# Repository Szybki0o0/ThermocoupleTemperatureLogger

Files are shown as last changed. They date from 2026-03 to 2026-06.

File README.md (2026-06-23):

# Thermocouple Temperature Logger

Projekt sprzętowo-programowy precyzyjnego wielokanałowego rejestratora temperatury. Urządzenie służy do odczytu, wyświetlania oraz logowania danych pomiarowych z maksymalnie 8 termopar.

## 📌 Opis Projektu

Głównym zadaniem układu jest akwizycja danych z czujników temperatury za pomocą dedykowanego układu **LTC2983**, a następnie ich przetwarzanie na mikrokontrolerze **STM32H5**. System oferuje możliwość lokalnego zapisu pomiarów na kartę pamięci lub przesyłania ich do komputera PC za pośrednictwem sieci Ethernet w popularnym standardzie automatyki pomiarowej (SCPI / VISA).

Projekt jest obecnie w fazie rozwoju i obejmuje zarówno projekt elektroniki (PCB), jak i oprogramowania układowego (Firmware).

## ✨ Główne funkcjonalności

* **Precyzyjny pomiar:** Odczyt temperatur z 8 niezależnych termopar przy użyciu specjalizowanego układu LTC2983.
* **Logowanie danych:** Zapis historii pomiarów bezpośrednio na kartę pamięci MicroSD.
* **Komunikacja z PC:** Zdalny odczyt i sterowanie przez interfejs Ethernet z wykorzystaniem protokołu **VISA / SCPI**.
* **Podgląd na żywo:** Wyświetlanie aktualnych temperatur oraz stanu urządzenia na monochromatycznym ekranie LCD/OLED.
* **Interfejs użytkownika (HMI):** Wygodne sterowanie za pomocą enkodera obrotowego oraz dedykowanych przycisków umieszczonych pod wyświetlaczem.

## 🛠️ Architektura Sprzętowa (Hardware)

* **Mikrokontroler:** Rodzina STM32H563ZI (ARM Cortex-M33)
* **Układ pomiarowy:** Analog Devices LTC2983 (Multi-Sensor High Accuracy Digital Temperature Measurement System)
* **Wyświetlacz:** Monochromatyczny LCD / OLED
* **Interfejsy:** 
    * Gniazdo Ethernet (RJ45)
    * Slot na kartę pamięci uSD
    * Konfigurowalny panel przedni do podłączenia czujników temperatory
* **Sterowanie lokalne:** Enkoder obrotowy z przyciskiem + przyciski funkcyjne pod ekranem.
* **Zasilanie:** Zasilacz 230VAC → 5VDC-12VDC w postaci gotowego modułu na PCB lub wykorzystanie zasilania przez gniazdo DC.

## 💻 Oprogramowanie (Software)

* **System operacyjny (RTOS):** Eclipse ThreadX
* **Stos sieciowy:** Obsługa Ethernet do komunikacji z systemami nadrzędnymi.
* **Protokół komunikacyjny:** SCPI (Standard Commands for Programmable Instruments).
* **System plików:** Obsługa FAT/exFAT dla karty SD.

## 🚀 Status projektu

Hardware:
- [x] Konfiguracją peryferiów dla STM32H5
- [X] Schemat
- [X] projekt PCB
- [X] Montaż PCB
- [~] Uruchomienie PCB

Software:
- [X] Integracja systemu operacyjnego ThreadX
- [ ] Napisanie sterownika do obsługi LTC2983
- [X] Implementacją parsera komend SCPI
- [ ] Opracowaniem UI

## ➗ Podział prac
- Mateusz Gąsiorowski: 
  - Konfiguracja Peryferiów STM32
  - Schemat
  - Projekt PCB
  - Montaż i uruchomienie
 
- Jakub Konior:
  - Konfiguracja Peryferiów STM32
  - Schemat
  - Oprogramowanie

---
*Autorzy: Mateusz Gąsiorowski && Jakub Konior*

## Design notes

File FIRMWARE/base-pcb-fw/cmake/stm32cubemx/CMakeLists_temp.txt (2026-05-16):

cmake_minimum_required(VERSION 3.22)# Enable CMake support for ASM and C languagesenable_language(C CXX ASM)# STM32CubeMX generated symbols (macros)set(MX_Defines_Syms 	NX_INCLUDE_USER_DEFINE_FILE 	TX_INCLUDE_USER_DEFINE_FILE 	TX_SINGLE_MODE_NON_SECURE=1 	USE_HAL_DRIVER 	STM32H563xx    $<$<CONFIG:Debug>:DEBUG>)# STM32CubeMX generated include pathsset(MX_Include_Dirs    ${CMAKE_CURRENT_SOURCE_DIR}/../../Core/Inc    ${CMAKE_CURRENT_SOURCE_DIR}/../../NetXDuo/App    ${CMAKE_CURRENT_SOURCE_DIR}/../../NetXDuo/Target    ${CMAKE_CURRENT_SOURCE_DIR}/../../AZURE_RTOS/App    ${CMAKE_CURRENT_SOURCE_DIR}/../../Drivers/STM32H5xx_HAL_Driver/Inc    ${CMAKE_CURRENT_SOURCE_DIR}/../../Drivers/STM32H5xx_HAL_Driver/Inc/Legacy    ${CMAKE_CURRENT_SOURCE_DIR}/../../Drivers/BSP/Components/lan8742    ${CMAKE_CURRENT_SOURCE_DIR}/../../Middlewares/ST/netxduo/common/drivers/ethernet    ${CMAKE_CURRENT_SOURCE_DIR}/../../Middlewares/ST/threadx/common/inc    ${CMAKE_CURRENT_SOURCE_DIR}/../../Drivers/CMSIS/Device/ST/STM32H5xx/Include    ${CMAKE_CURRENT_SOURCE_DIR}/../../Middlewares/ST/netxduo/common/inc    ${CMAKE_CURRENT_SOURCE_DIR}/../../Middlewares/ST/netxduo/ports/cortex_m33/gnu/inc    ${CMAKE_CURRENT_SOURCE_DIR}/../../Middlewares/ST/threadx/ports/cortex_m33/gnu/inc    ${CMAKE_CURRENT_SOURCE_DIR}/../../Drivers/CMSIS/Include)# STM32CubeMX generated application sourcesset(MX_Application_Src    ${CMAKE_CURRENT_SOURCE_DIR}/../../NetXDuo/App/app_netxduo.c    ${CMAKE_CURRENT_SOURCE_DIR}/../../AZURE_RTOS/App/app_azure_rtos.c    ${CMAKE_CURRENT_SOURCE_DIR}/../../Core/Src/tx_initialize_low_level.S    ${CMAKE_CURRENT_SOURCE_DIR}/../../Core/Src/main.cpp    ${CMAKE_CURRENT_SOURCE_DIR}/../../Core/Src/gpio.c    ${CMAKE_CURRENT_SOURCE_DIR}/../../Core/Src/eth.c    ${CMAKE_CURRENT_SOURCE_DIR}/../../Core/Src/gpdma.c    ${CMAKE_CURRENT_SOURCE_DIR}/../../Core/Src/i2c.c    ${CMAKE_CURRENT_SOURCE_DIR}/../../Core/Src/sdmmc.c    ${CMAKE_CURRENT_SOURCE_DIR}/../../Core/Src/spi.c    ${CMAKE_CURRENT_SOURCE_DIR}/../../Core/Src/app_threadx.c    ${CMAKE_CURRENT_SOURCE_DIR}/../../Core/Src/tim.c    ${CMAKE_CURRENT_SOURCE_DIR}/../../Core/Src/stm32h5xx_it.c    ${CMAKE_CURRENT_SOURCE_DIR}/../../Core/Src/stm32h5xx_hal_msp.c    ${CMAKE_CURRENT_SOURCE_DIR}/../../Core/Src/sysmem.c    ${CMAKE_CURRENT_SOURCE_DIR}/../../Core/Src/syscalls.c    ${CMAKE_CURRENT_SOURCE_DIR}/../../startup_stm32h563xx.s)# STM32 HAL/LL Driversset(STM32_Drivers_Src    ${CMAKE_CURRENT_SOURCE_DIR}/../../Core/Src/system_stm32h5xx.c    ${CMAKE_CURRENT_SOURCE_DIR}/../../Drivers/STM32H5xx_HAL_Driver/Src/stm32h5xx_hal_cortex.c    ${CMAKE_CURRENT_SOURCE_DIR}/../../Drivers/STM32H5xx_HAL_Driver/Src/stm32h5xx_hal_rcc.c    ${CMAKE_CURRENT_SOURCE_DIR}/../../Drivers/STM32H5xx_HAL_Driver/Src/stm32h5xx_hal_rcc_ex.c    ${CMAKE_CURRENT_SOURCE_DIR}/../../Drivers/STM32H5xx_HAL_Driver/Src/stm32h5xx_hal_flash.c    ${CMAKE_CURRENT_SOURCE_DIR}/../../Drivers/STM32H5xx_HAL_Driver/Src/stm32h5xx_hal_flash_ex.c    ${CMAKE_CURRENT_SOURCE_DIR}/../../Drivers/STM32H5xx_HAL_Driver/Src/stm32h5xx_hal_gpio.c    ${CMAKE_CURRENT_SOURCE_DIR}/../../Drivers/STM32H5xx_HAL_Driver/Src/stm32h5xx_hal_dma.c    ${CMAKE_CURRENT_SOURCE_DIR}/../../Drivers/STM32H5xx_HAL_Driver/Src/stm32h5xx_hal_dma_ex.c    ${CMAKE_CURRENT_SOURCE_DIR}/../../Drivers/STM32H5xx_HAL_Driver/Src/stm32h5xx_hal_pwr.c    ${CMAKE_CURRENT_SOURCE_DIR}/../../Drivers/STM32H5xx_HAL_Driver/Src/stm32h5xx_hal_pwr_ex.c    ${CMAKE_CURRENT_SOURCE_DIR}/../../Drivers/STM32H5xx_HAL_Driver/Src/stm32h5xx_hal.c    ${CMAKE_CURRENT_SOURCE_DIR}/../../Drivers/STM32H5xx_HAL_Driver/Src/stm32h5xx_hal_exti.c    ${CMAKE_CURRENT_SOURCE_DIR}/../../Drivers/STM32H5xx_HAL_Driver/Src/stm32h5xx_hal_eth.c    ${CMAKE_CURRENT_SOURCE_DIR}/../../Drivers/STM32H5xx_HAL_Driver/Src/stm32h5xx_hal_eth_ex.c    ${CMAKE_CURRENT_SOURCE_DIR}/../../Drivers/STM32H5xx_HAL_Driver/Src/stm32h5xx_hal_i2c.c    ${CMAKE_CURRENT_SOURCE_DIR}/../../Drivers/STM32H5xx_HAL_Driver/Src/stm32h5xx_hal_i2c_ex.c    ${CMAKE_CURRENT_SOURCE_DIR}/../../Drivers/STM32H5xx_HAL_Driver/Src/stm32h5xx_ll_sdmmc.c    ${CMAKE_CURRENT_SOURCE_DIR}/../../Drivers/STM32H5xx_HAL_Driver/Src/stm32h5xx_ll_dlyb.c    ${CMAKE_CURRENT_SOURCE_DIR}/../../Drivers/STM32H5xx_HAL_Driver/Src/stm32h5xx_hal_sd.c    ${CMAKE_CURRENT_SOURCE_DIR}/../../Drivers/STM32H5xx_HAL_Driver/Src/stm32h5xx_hal_sd_ex.c    ${CMAKE_CURRENT_SOURCE_DIR}/../../Drivers/STM32H5xx_HAL_Driver/Src/stm32h5xx_hal_mmc.c    ${CMAKE_CURRENT_SOURCE_DIR}/../../Drivers/STM32H5xx_HAL_Driver/Src/stm32h5xx_hal_mmc_ex.c    ${CMAKE_CURRENT_SOURCE_DIR}/../../Drivers/STM32H5xx_HAL_Driver/Src/stm32h5xx_hal_sdio.c    ${CMAKE_CURRENT_SOURCE_DIR}/../../Drivers/STM32H5xx_HAL_Driver/Src/stm32h5xx_hal_spi.c    ${CMAKE_CURRENT_SOURCE_DIR}/../../Drivers/STM32H5xx_HAL_Driver/Src/stm32h5xx_hal_spi_ex.c    ${CMAKE_CURRENT_SOURCE_DIR}/../../Drivers/STM32H5xx_HAL_Driver/Src/stm32h5xx_hal_tim.c    ${CMAKE_CURRENT_SOURCE_DIR}/../../Drivers/STM32H5xx_HAL_Driver/Src/stm32h5xx_hal_tim_ex.c    ${CMAKE_CURRENT_SOURCE_DIR}/../../Drivers/BSP/Components/lan8742/lan8742.c)# Drivers Midllewaresset(ThreadX_Src    ${CMAKE_CURRENT_SOURCE_DIR}/../../Middlewares/ST/threadx/ports/cortex_m33/gnu/src/tx_thread_context_restore.S    ${CMAKE_CURRENT_SOURCE_DIR}/../../Middlewares/ST/threadx/ports/cortex_m33/gnu/src/tx_thread_context_save.S    ${CMAKE_CURRENT_SOURCE_DIR}/../../Middlewares/ST/threadx/ports/cortex_m33/gnu/src/tx_thread_interrupt_control.S    ${CMAKE_CURRENT_SOURCE_DIR}/../../Middlewares/ST/threadx/ports/cortex_m33/gnu/src/tx_thread_interrupt_disable.S    ${CMAKE_CURRENT_SOURCE_DIR}/../../Middlewares/ST/threadx/ports/cortex_m33/gnu/src/tx_thread_interrupt_restore.S    ${CMAKE_CURRENT_SOURCE_DIR}/../../Middlewares/ST/threadx/ports/cortex_m33/gnu/src/tx_thread_schedule.S    ${CMAKE_CURRENT_SOURCE_DIR}/../../Middlewares/ST/threadx/ports/cortex_m33/gnu/src/tx_thread_stack_build.S    ${CMAKE_CURRENT_SOURCE_DIR}/../../Middlewares/ST/threadx/ports/cortex_m33/gnu/src/tx_thread_system_return.S    ${CMAKE_CURRENT_SOURCE_DIR}/../../Middlewares/ST/threadx/ports/cortex_m33/gnu/src/tx_timer_interrupt.S    ${CMAKE_CURRENT_SOURCE_DIR}/../../Middlewares/ST/threadx/common/src/tx_initialize_high_level.c    ${CMAKE_CURRENT_SOURCE_DIR}/../../Middlewares/ST/threadx/common/src/tx_initialize_kernel_enter.c    ${CMAKE_CURRENT_SOURCE_DIR}/../../Middlewares/ST/threadx/common/src/tx_initialize_kernel_setup.c    ${CMAKE_CURRENT_SOURCE_DIR}/../../Middlewares/ST/threadx/common/src/tx_thread_stack_error_handler.c    ${CMAKE_CURRENT_SOURCE_DIR}/../../Middlewares/ST/threadx/common/src/tx_thread_stack_error_notify.c    ${CMAKE_CURRENT_SOURCE_DIR}/../../Middlewares/ST/threadx/common/src/tx_thread_system_resume.c    ${CMAKE_CURRENT_SOURCE_DIR}/../../Middlewares/ST/threadx/common/src/tx_block_allocate.c    ${CMAKE_CURRENT_SOURCE_DIR}/../../Middlewares/ST/threadx/common/src/tx_block_pool_cleanup.c    ${CMAKE_CURRENT_SOURCE_DIR}/../../Middlewares/ST/threadx/common/src/tx_block_pool_create.c    ${CMAKE_CURRENT_SOURCE_DIR}/../../Middlewares/ST/threadx/common/src/tx_block_pool_delete.c    ${CMAKE_CURRENT_SOURCE_DIR}/../../Middlewares/ST/threadx/common/src/tx_block_pool_info_get.c    ${CMAKE_CURRENT_SOURCE_DIR}/../../Middlewares/ST/threadx/common/src/tx_block_pool_initialize.c    ${CMAKE_CURRENT_SOURCE_DIR}/../../Middlewares/ST/threadx/common/src/tx_block_pool_prioritize.c    ${CMAKE_CURRENT_SOURCE_DIR}/../../Middlewares/ST/threadx/common/src/tx_block_release.c    ${CMAKE_CURRENT_SOURCE_DIR}/../../Middlewares/ST/threadx/common/src/tx_byte_allocate.c    ${CMAKE_CURRENT_SOURCE_DIR}/../../Middlewares/ST/threadx/common/src/tx_byte_pool_cleanup.c    ${CMAKE_CURRENT_SOURCE_DIR}/../../Middlewares/ST/threadx/common/src/tx_byte_pool_create.c    ${CMAKE_CURRENT_SOURCE_DIR}/../../Middlewares/ST/threadx/common/src/tx_byte_pool_delete.c    ${CMAKE_CURRENT_SOURCE_DIR}/../../Middlewares/ST/threadx/common/src/tx_byte_pool_info_get.c    ${CMAKE_CURRENT_SOURCE_DIR}/../../Middlewares/ST/threadx/common/src/tx_byte_pool_initialize.c    ${CMAKE_CURRENT_SOURCE_DIR}/../../Middlewares/ST/threadx/common/src/tx_byte_pool_prioritize.c    ${CMAKE_CURRENT_SOURCE_DIR}/../../Middlewares/ST/threadx/common/src/tx_byte_pool_search.c    ${CMAKE_CURRENT_SOURCE_DIR}/../../Middlewares/ST/threadx/common/src/tx_byte_release.c    ${CMAKE_CURRENT_SOURCE_DIR}/../../Middlewares/ST/threadx/common/src/tx_event_flags_cleanup.c    ${CMAKE_CURRENT_SOURCE_DIR}/../../Middlewares/ST/threadx/common/src/tx_event_flags_create.c    ${CMAKE_CURRENT_SOURCE_DIR}/../../Middlewares/ST/threadx/common/src/tx_event_flags_delete.c    ${CMAKE_CURRENT_SOURCE_DIR}/../../Middlewares/ST/threadx/common/src/tx_event_flags_get.c    ${CMAKE_CURRENT_SOURCE_DIR}/../../Middlewares/ST/threadx/common/src/tx_event_flags_info_get.c    ${CMAKE_CURRENT_SOURCE_DIR}/../../Middlewares/ST/threadx/common/src/tx_event_flags_initialize.c    ${CMAKE_CURRENT_SOURCE_DIR}/../../Middlewares/ST/threadx/common/src/tx_event_flags_set.c    ${CMAKE_CURRENT_SOURCE_DIR}/../../Middlewares/ST/threadx/common/src/tx_event_flags_set_notify.c    ${CMAKE_CURRENT_SOURCE_DIR}/../../Middlewares/ST/threadx/common/src/tx_mutex_cleanup.c    ${CMAKE_CURRENT_SOURCE_DIR}/../../Middlewares/ST/threadx/common/src/tx_mutex_create.c    ${CMAKE_CURRENT_SOURCE_DIR}/../../Middlewares/ST/threadx/common/src/tx_mutex_delete.c    ${CMAKE_CURRENT_SOURCE_DIR}/../../Middlewares/ST/threadx/common/src/tx_mutex_get.c    ${CMAKE_CURRENT_SOURCE_DIR}/../../Middlewares/ST/threadx/common/src/tx_mutex_info_get.c    ${CMAKE_CURRENT_SOURCE_DIR}/../../Middlewares/ST/threadx/common/src/tx_mutex_initialize.c    ${CMAKE_CURRENT_SOURCE_DIR}/../../Middlewares/ST/threadx/common/src/tx_mutex_prioritize.c    ${CMAKE_CURRENT_SOURCE_DIR}/../../Middlewares/ST/threadx/common/src/tx_mutex_priority_change.c    ${CMAKE_CURRENT_SOURCE_DIR}/../../Middlewares/ST/threadx/common/src/tx_mutex_put.c    ${CMAKE_CURRENT_SOURCE_DIR}/../../Middlewares/ST/threadx/common/src/tx_queue_cleanup.c    ${CMAKE_CURRENT_SOURCE_DIR}/../../Middlewares/ST/threadx/common/src/tx_queue_create.c    ${CMAKE_CURRENT_SOURCE_DIR}/../../Middlewares/ST/threadx/common/src/tx_queue_delete.c    ${CMAKE_CURRENT_SOURCE_DIR}/../../Middlewares/ST/threadx/common/src/tx_queue_flush.c    ${CMAKE_CURRENT_SOURCE_DIR}/../../Middlewares/ST/threadx/common/src/tx_queue_front_send.c    ${CMAKE_CURRENT_SOURCE_DIR}/../../Middlewares/ST/threadx/common/src/tx_queue_info_get.c    ${CMAKE_CURRENT_SOURCE_DIR}/../../Middlewares/ST/threadx/common/src/tx_queue_initialize.c    ${CMAKE_CURRENT_SOURCE_DIR}/../../Middlewares/ST/threadx/common/src/tx_queue_prioritize.c    ${CMAKE_CURRENT_SOURCE_DIR}/../../Middlewares/ST/threadx/common/src/tx_queue_receive.c    ${CMAKE_CURRENT_SOURCE_DIR}/../../Middlewares/ST/threadx/common/src/tx_queue_send.c    ${CMAKE_CURRENT_SOURCE_DIR}/../../Middlewares/ST/threadx/common/src/tx_queue_send_notify.c    ${CMAKE_CURRENT_SOURCE_DIR}/../../Middlewares/ST/threadx/common/src/tx_semaphore_ceiling_put.c    ${CMAKE_CURRENT_SOURCE_DIR}/../../Middlewares/ST/threadx/common/src/tx_semaphore_cleanup.c    ${CMAKE_CURRENT_SOURCE_DIR}/../../Middlewares/ST/threadx/common/src/tx_semaphore_create.c    ${CMAKE_CURRENT_SOURCE_DIR}/../../Middlewares/ST/threadx/common/src/tx_semaphore_delete.c    ${CMAKE_CURRENT_SOURCE_DIR}/../../Middlewares/ST/threadx/common/src/tx_semaphore_get.c    ${CMAKE_CURRENT_SOURCE_DIR}/../../Middlewares/ST/threadx/common/src/tx_semaphore_info_get.c    ${CMAKE_CURRENT_SOURCE_DIR}/../../Middlewares/ST/threadx/common/src/tx_semaphore_initialize.c    ${CMAKE_CURRENT_SOURCE_DIR}/../../Middlewares/ST/threadx/common/src/tx_semaphore_prioritize.c    ${CMAKE_CURRENT_SOURCE_DIR}/../../Middlewares/ST/threadx/common/src/tx_semaphore_put.c    ${CMAKE_CURRENT_SOURCE_DIR}/../../Middlewares/ST/threadx/common/src/tx_semaphore_put_notify.c    ${CMAKE_CURRENT_SOURCE_DIR}/../../Middlewares/ST/threadx/common/src/tx_thread_create.c    ${CMAKE_CURRENT_SOURCE_DIR}/../../Middlewares/ST/threadx/common/src/tx_thread_delete.c    ${CMAKE_CURRENT_SOURCE_DIR}/../../Middlewares/ST/threadx/common/src/tx_thread_entry_exit_notify.c    ${CMAKE_CURRENT_SOURCE_DIR}/../../Middlewares/ST/threadx/common/src/tx_thread_identify.c    ${CMAKE_CURRENT_SOURCE_DIR}/../../Middlewares/ST/threadx/common/src/tx_thread_info_get.c    ${CMAKE_CURRENT_SOURCE_DIR}/../../Middlewares/ST/threadx/common/src/tx_thread_initialize.c    ${CMAKE_CURRENT_SOURCE_DIR}/../../Middlewares/ST/threadx/common/src/tx_thread_preemption_change.c    ${CMAKE_CURRENT_SOURCE_DIR}/../../Middlewares/ST/threadx/common/src/tx_thread_priority_change.c    ${CMAKE_CURRENT_SOURCE_DIR}/../../Middlewares/ST/threadx/common/src/tx_thread_relinquish.c    ${CMAKE_CURRENT_SOURCE_DIR}/../../Middlewares/ST/threadx/common/src/tx_thread_reset.c    ${CMAKE_CURRENT_SOURCE_DIR}/../../Middlewares/ST/threadx/common/src/tx_thread_resume.c    ${CMAKE_CURRENT_SOURCE_DIR}/../../Middlewares/ST/threadx/common/src/tx_thread_shell_entry.c    ${CMAKE_CURRENT_SOURCE_DIR}/../../Middlewares/ST/threadx/common/src/tx_thread_sleep.c    ${CMAKE_CURRENT_SOURCE_DIR}/../../Middlewares/ST/threadx/common/src/tx_thread_stack_analyze.c    ${CMAKE_CURRENT_SOURCE_DIR}/../../Middlewares/ST/threadx/common/src/tx_thread_suspend.c    ${CMAKE_CURRENT_SOURCE_DIR}/../../Middlewares/ST/threadx/common/src/tx_thread_system_preempt_check.c    ${CMAKE_CURRENT_SOURCE_DIR}/../../Middlewares/ST/threadx/common/src/tx_thread_system_suspend.c    ${CMAKE_CURRENT_SOURCE_DIR}/../../Middlewares/ST/threadx/common/src/tx_thread_terminate.c    ${CMAKE_CURRENT_SOURCE_DIR}/../../Middlewares/ST/threadx/common/src/tx_thread_time_slice.c    ${CMAKE_CURRENT_SOURCE_DIR}/../../Middlewares/ST/threadx/common/src/tx_thread_time_slice_change.c    ${CMAKE_CURRENT_SOURCE_DIR}/../../Middlewares/ST/threadx/common/src/tx_thread_timeout.c    ${CMAKE_CURRENT_SOURCE_DIR}/../../Middlewares/ST/threadx/common/src/tx_thread_wait_abort.c    ${CMAKE_CURRENT_SOURCE_DIR}/../../Middlewares/ST/threadx/common/src/tx_time_get.c    ${CMAKE_CURRENT_SOURCE_DIR}/../../Middlewares/ST/threadx/common/src/tx_time_set.c    ${CMAKE_CURRENT_SOURCE_DIR}/../../Middlewares/ST/threadx/common/src/txe_block_allocate.c    ${CMAKE_CURRENT_SOURCE_DIR}/../../Middlewares/ST/threadx/common/src/txe_block_pool_create.c    ${CMAKE_CURRENT_SOURCE_DIR}/../../Middlewares/ST/threadx/common/src/txe_block_pool_delete.c    ${CMAKE_CURRENT_SOURCE_DIR}/../../Middlewares/ST/threadx/common/src/txe_block_pool_info_get.c    ${CMAKE_CURRENT_SOURCE_DIR}/../../Middlewares/ST/threadx/common/src/txe_block_pool_prioritize.c    ${CMAKE_CURRENT_SOURCE_DIR}/../../Middlewares/ST/threadx/common/src/txe_block_release.c    ${CMAKE_CURRENT_SOURCE_DIR}/../../Middlewares/ST/threadx/common/src/txe_byte_allocate.c    ${CMAKE_CURRENT_SOURCE_DIR}/../../Middlewares/ST/threadx/common/src/txe_byte_pool_create.c    ${CMAKE_CURRENT_SOURCE_DIR}/../../Middlewares/ST/threadx/common/src/txe_byte_pool_delete.c    ${CMAKE_CURRENT_SOURCE_DIR}/../../Middlewares/ST/threadx/common/src/txe_byte_pool_info_get.c    ${CMAKE_CURRENT_SOURCE_DIR}/../../Middlewares/ST/threadx/common/src/txe_byte_pool_prioritize.c    ${CMAKE_CURRENT_SOURCE_DIR}/../../Middlewares/ST/threadx/common/src/txe_byte_release.c    ${CMAKE_CURRENT_SOURCE_DIR}/../../Middlewares/ST/threadx/common/src/txe_event_flags_create.c    ${CMAKE_CURRENT_SOURCE_DIR}/../../Middlewares/ST/threadx/common/src/txe_event_flags_delete.c    ${CMAKE_CURRENT_SOURCE_DIR}/../../Middlewares/ST/threadx/common/src/txe_event_flags_get.c    ${CMAKE_CURRENT_SOURCE_DIR}/../../Middlewares/ST/threadx/common/src/txe_event_flags_info_get.c    ${CMAKE_CURRENT_SOURCE_DIR}/../../Middlewares/ST/threadx/common/src/txe_event_flags_set.c    ${CMAKE_CURRENT_SOURCE_DIR}/../../Middlewares/ST/threadx/common/src/txe_event_flags_set_notify.c    ${CMAKE_CURRENT_SOURCE_DIR}/../../Middlewares/ST/threadx/common/src/txe_mutex_create.c    ${CMAKE_CURRENT_SOURCE_DIR}/../../Middlewares/ST/threadx/common/src/txe_mutex_delete.c    ${CMAKE_CURRENT_SOURCE_DIR}/../../Middlewares/ST/threadx/common/src/txe_mutex_get.c    ${CMAKE_CURRENT_SOURCE_DIR}/../../Middlewares/ST/threadx/common/src/txe_mutex_info_get.c    ${CMAKE_CURRENT_SOURCE_DIR}/../../Middlewares/ST/threadx/common/src/txe_mutex_prioritize.c    ${CMAKE_CURRENT_SOURCE_DIR}/../../Middlewares/ST/threadx/common/src/txe_mutex_put.c    ${CMAKE_CURRENT_SOURCE_DIR}/../../Middlewares/ST/threadx/common/src/txe_queue_create.c    ${CMAKE_CURRENT_SOURCE_DIR}/../../Middlewares/ST/threadx/common/src/txe_queue_delete.c    ${CMAKE_CURRENT_SOURCE_DIR}/../../Middlewares/ST/threadx/common/src/txe_queue_flush.c    ${CMAKE_CURRENT_SOURCE_DIR}/../../Middlewares/ST/threadx/common/src/txe_queue_front_send.c    ${CMAKE_CURRENT_SOURCE_DIR}/../../Middlewares/ST/threadx/common/src/txe_queue_info_get.c    ${CMAKE_CURRENT_SOURCE_DIR}/../../Middlewares/ST/threadx/common/src/txe_queue_prioritize.c    ${CMAKE_CURRENT_SOURCE_DIR}/../../Middlewares/ST/threadx/common/src/txe_queue_receive.c    ${CMAKE_CURRENT_SOURCE_DIR}/../../Middlewares/ST/threadx/common/src/txe_queue_send.c    ${CMAKE_CURRENT_SOURCE_DIR}/../../Middlewares/ST/threadx/common/src/txe_queue_send_notify.c    ${CMAKE_CURRENT_SOURCE_DIR}/../../Middlewares/ST/threadx/common/src/txe_semaphore_ceiling_put.c    ${CMAKE_CURRENT_SOURCE_DIR}/../../Middlewares/ST/threadx/common/src/txe_semaphore_create.c    ${CMAKE_CURRENT_SOURCE_DIR}/../../Middlewares/ST/threadx/common/src/txe_semaphore_delete.c    ${CMAKE_CURRENT_SOURCE_DIR}/../../Middlewares/ST/threadx/common/src/txe_semaphore_get.c    ${CMAKE_CURRENT_SOURCE_DIR}/../../Middlewares/ST/threadx/common/src/txe_semaphore_info_get.c    ${CMAKE_CURRENT_SOURCE_DIR}/../../Middlewares/ST/threadx/common/src/txe_semaphore_prioritize.c    ${CMAKE_CURRENT_SOURCE_DIR}/../../Middlewares/ST/threadx/common/src/txe_semaphore_put.c    ${CMAKE_CURRENT_SOURCE_DIR}/../../Middlewares/ST/threadx/common/src/txe_semaphore_put_notify.c    ${CMAKE_CURRENT_SOURCE_DIR}/../../Middlewares/ST/threadx/common/src/txe_thread_create.c    ${CMAKE_CURRENT_SOURCE_DIR}/../../Middlewares/ST/threadx/common/src/txe_thread_delete.c    ${CMAKE_CURRENT_SOURCE_DIR}/../../Middlewares/ST/threadx/common/src/txe_thread_entry_exit_notify.c    ${CMAKE_CURRENT_SOURCE_DIR}/../../Middlewares/ST/threadx/common/src/txe_thread_info_get.c    ${CMAKE_CURRENT_SOURCE_DIR}/../../Middlewares/ST/threadx/common/src/txe_thread_preemption_change.c    ${CMAKE_CURRENT_SOURCE_DIR}/../../Middlewares/ST/threadx/common/src/txe_thread_priority_change.c    ${CMAKE_CURRENT_SOURCE_DIR}/../../Middlewares/ST/threadx/common/src/txe_thread_relinquish.c    ${CMAKE_CURRENT_SOURCE_DIR}/../../Middlewares/ST/threadx/common/src/txe_thread_reset.c    ${CMAKE_CURRENT_SOURCE_DIR}/../../Middlewares/ST/threadx/common/src/txe_thread_resume.c    ${CMAKE_CURRENT_SOURCE_DIR}/../../Middlewares/ST/threadx/common/src/txe_thread_suspend.c    ${CMAKE_CURRENT_SOURCE_DIR}/../../Middlewares/ST/threadx/common/src/txe_thread_terminate.c    ${CMAKE_CURRENT_SOURCE_DIR}/../../Middlewares/ST/threadx/common/src/txe_thread_time_slice_change.c    ${CMAKE_CURRENT_SOURCE_DIR}/../../Middlewares/ST/threadx/common/src/txe_thread_wait_abort.c    ${CMAKE_CURRENT_SOURCE_DIR}/../../Middlewares/ST/threadx/common/src/tx_timer_activate.c    ${CMAKE_CURRENT_SOURCE_DIR}/../../Middlewares/ST/threadx/common/src/tx_timer_change.c    ${CMAKE_CURRENT_SOURCE_DIR}/../../Middlewares/ST/threadx/common/src/tx_timer_create.c    ${CMAKE_CURRENT_SOURCE_DIR}/../../Middlewares/ST/threadx/common/src/tx_timer_deactivate.c    ${CMAKE_CURRENT_SOURCE_DIR}/../../Middlewares/ST/threadx/common/src/tx_timer_delete.c    ${CMAKE_CURRENT_SOURCE_DIR}/../../Middlewares/ST/threadx/common/src/tx_timer_expiration_process.c    ${CMAKE_CURRENT_SOURCE_DIR}/../../Middlewares/ST/threadx/common/src/tx_timer_info_get.c    ${CMAKE_CURRENT_SOURCE_DIR}/../../Middlewares/ST/threadx/common/src/tx_timer_initialize.c    ${CMAKE_CURRENT_SOURCE_DIR}/../../Middlewares/ST/threadx/common/src/tx_timer_system_activate.c    ${CMAKE_CURRENT_SOURCE_DIR}/../../Middlewares/ST/threadx/common/src/tx_timer_system_deactivate.c    ${CMAKE_CURRENT_SOURCE_DIR}/../../Middlewares/ST/threadx/common/src/tx_timer_thread_entry.c    ${CMAKE_CURRENT_SOURCE_DIR}/../../Middlewares/ST/threadx/common/src/txe_timer_activate.c    ${CMAKE_CURRENT_SOURCE_DIR}/../../Middlewares/ST/threadx/common/src/txe_timer_change.c    ${CMAKE_CURRENT_SOURCE_DIR}/../../Middlewares/ST/threadx/common/src/txe_timer_create.c    ${CMAKE_CURRENT_SOURCE_DIR}/../../Middlewares/ST/threadx/common/src/txe_timer_deactivate.c    ${CMAKE_CURRENT_SOURCE_DIR}/../../Middlewares/ST/threadx/common/src/txe_timer_delete.c    ${CMAKE_CURRENT_SOURCE_DIR}/../../Middlewares/ST/threadx/common/src/txe_timer_info_get.c)set(NetXDuo_Src    ${CMAKE_CURRENT_SOURCE_DIR}/../../Middlewares/ST/netxduo/common/drivers/ethernet/nx_stm32_eth_driver.c    ${CMAKE_CURRENT_SOURCE_DIR}/../../Middlewares/ST/netxduo/common/src/nx_arp_announce_send.c    ${CMAKE_CURRENT_SOURCE_DIR}/../../Middlewares/ST/netxduo/common/src/nx_arp_dynamic_entries_invalidate.c    ${CMAKE_CURRENT_SOURCE_DIR}/../../Middlewares/ST/netxduo/common/src/nx_arp_dynamic_entry_delete.c    ${CMAKE_CURRENT_SOURCE_DIR}/../../Middlewares/ST/netxduo/common/src/nx_arp_dynamic_entry_set.c    ${CMAKE_CURRENT_SOURCE_DIR}/../../Middlewares/ST/netxduo/common/src/nx_arp_enable.c    ${CMAKE_CURRENT_SOURCE_DIR}/../../Middlewares/ST/netxduo/common/src/nx_arp_entry_allocate.c    ${CMAKE_CURRENT_SOURCE_DIR}/../../Middlewares/ST/netxduo/common/src/nx_arp_entry_delete.c    ${CMAKE_CURRENT_SOURCE_DIR}/../../Middlewares/ST/netxduo/common/src/nx_arp_gratuitous_send.c    ${CMAKE_CURRENT_SOURCE_DIR}/../../Middlewares/ST/netxduo/common/src/nx_arp_hardware_address_find.c    ${CMAKE_CURRENT_SOURCE_DIR}/../../Middlewares/ST/netxduo/common/src/nx_arp_info_get.c    ${CMAKE_CURRENT_SOURCE_DIR}/../../Middlewares/ST/netxduo/common/src/nx_arp_initialize.c    ${CMAKE_CURRENT_SOURCE_DIR}/../../Middlewares/ST/netxduo/common/src/nx_arp_interface_entries_delete.c    ${CMAKE_CURRENT_SOURCE_DIR}/../../Middlewares/ST/netxduo/common/src/nx_arp_ip_address_find.c    ${CMAKE_CURRENT_SOURCE_DIR}/../../Middlewares/ST/netxduo/common/src/nx_arp_packet_deferred_receive.c    ${CMAKE_CURRENT_SOURCE_DIR}/../../Middlewares/ST/netxduo/common/src/nx_arp_packet_receive.c    ${CMAKE_CURRENT_SOURCE_DIR}/../../Middlewares/ST/netxduo/common/src/nx_arp_packet_send.c    ${CMAKE_CURRENT_SOURCE_DIR}/../../Middlewares/ST/netxduo/common/src/nx_arp_periodic_update.c    ${CMAKE_CURRENT_SOURCE_DIR}/../../Middlewares/ST/netxduo/common/src/nx_arp_probe_send.c    ${CMAKE_CURRENT_SOURCE_DIR}/../../Middlewares/ST/netxduo/common/src/nx_arp_queue_process.c    ${CMAKE_CURRENT_SOURCE_DIR}/../../Middlewares/ST/netxduo/common/src/nx_arp_queue_send.c    ${CMAKE_CURRENT_SOURCE_DIR}/../../Middlewares/ST/netxduo/common/src/nx_arp_static_entries_delete.c    ${CMAKE_CURRENT_SOURCE_DIR}/../../Middlewares/ST/netxduo/common/src/nx_arp_static_entry_create.c    ${CMAKE_CURRENT_SOURCE_DIR}/../../Middlewares/ST/netxduo/common/src/nx_arp_static_entry_delete.c    ${CMAKE_CURRENT_SOURCE_DIR}/../../Middlewares/ST/netxduo/common/src/nx_arp_static_entry_delete_internal.c    ${CMAKE_CURRENT_SOURCE_DIR}/../../Middlewares/ST/netxduo/common/src/nx_icmp_cleanup.c    ${CMAKE_CURRENT_SOURCE_DIR}/../../Middlewares/ST/netxduo/common/src/nx_icmp_enable.c    ${CMAKE_CURRENT_SOURCE_DIR}/../../Middlewares/ST/netxduo/common/src/nx_icmp_info_get.c    ${CMAKE_CURRENT_SOURCE_DIR}/../../Middlewares/ST/netxduo/common/src/nx_icmp_interface_ping.c    ${CMAKE_CURRENT_SOURCE_DIR}/../../Middlewares/ST/netxduo/common/src/nx_icmp_interface_ping6.c    ${CMAKE_CURRENT_SOURCE_DIR}/../../Middlewares/ST/netxduo/common/src/nx_icmp_packet_process.c    ${CMAKE_CURRENT_SOURCE_DIR}/../../Middlewares/ST/netxduo/common/src/nx_icmp_packet_receive.c    ${CMAKE_CURRENT_SOURCE_DIR}/../../Middlewares/ST/netxduo/common/src/nx_icmp_ping.c    ${CMAKE_CURRENT_SOURCE_DIR}/../../Middlewares/ST/netxduo/common/src/nx_icmp_queue_process.c    ${CMAKE_CURRENT_SOURCE_DIR}/../../Middlewares/ST/netxduo/common/src/nx_icmpv4_packet_process.c    ${CMAKE_CURRENT_SOURCE_DIR}/../../Middlewares/ST/netxduo/common/src/nx_icmpv4_process_echo_reply.c    ${CMAKE_CURRENT_SOURCE_DIR}/../../Middlewares/ST/netxduo/common/src/nx_icmpv4_process_echo_request.c    ${CMAKE_CURRENT_SOURCE_DIR}/../../Middlewares/ST/netxduo/common/src/nx_icmpv4_send_error_message.c    ${CMAKE_CURRENT_SOURCE_DIR}/../../Middlewares/ST/netxduo/common/src/nx_igmp_enable.c    ${CMAKE_CURRENT_SOURCE_DIR}/../../Middlewares/ST/netxduo/common/src/nx_igmp_info_get.c    ${CMAKE_CURRENT_SOURCE_DIR}/../../Middlewares/ST/netxduo/common/src/nx_igmp_interface_report_send.c    ${CMAKE_CURRENT_SOURCE_DIR}/../../Middlewares/ST/netxduo/common/src/nx_igmp_loopback_disable.c    ${CMAKE_CURRENT_SOURCE_DIR}/../../Middlewares/ST/netxduo/common/src/nx_igmp_loopback_enable.c    ${CMAKE_CURRENT_SOURCE_DIR}/../../Middlewares/ST/netxduo/common/src/nx_igmp_multicast_check.c    ${CMAKE_CURRENT_SOURCE_DIR}/../../Middlewares/ST/netxduo/common/src/nx_igmp_multicast_interface_join.c    ${CMAKE_CURRENT_SOURCE_DIR}/../../Middlewares/ST/netxduo/common/src/nx_igmp_multicast_interface_join_internal.c    ${CMAKE_CURRENT_SOURCE_DIR}/../../Middlewares/ST/netxduo/common/src/nx_igmp_multicast_interface_leave.c    ${CMAKE_CURRENT_SOURCE_DIR}/../../Middlewares/ST/netxduo/common/src/nx_igmp_multicast_interface_leave_internal.c    ${CMAKE_CURRENT_SOURCE_DIR}/../../Middlewares/ST/netxduo/common/src/nx_igmp_multicast_join.c    ${CMAKE_CURRENT_SOURCE_DIR}/../../Middlewares/ST/netxduo/common/src/nx_igmp_multicast_leave.c    ${CMAKE_CURRENT_SOURCE_DIR}/../../Middlewares/ST/netxduo/common/src/nx_igmp_packet_process.c    ${CMAKE_CURRENT_SOURCE_DIR}/../../Middlewares/ST/netxduo/common/src/nx_igmp_packet_receive.c    ${CMAKE_CURRENT_SOURCE_DIR}/../../Middlewares/ST/netxduo/common/src/nx_igmp_periodic_processing.c    ${CMAKE_CURRENT_SOURCE_DIR}/../../Middlewares/ST/netxduo/common/src/nx_igmp_queue_process.c    ${CMAKE_CURRENT_SOURCE_DIR}/../../Middlewares/ST/netxduo/common/src/nx_invalidate_destination_entry.c    ${CMAKE_CURRENT_SOURCE_DIR}/../../Middlewares/ST/netxduo/common/src/nx_ip_address_change_notify.c    ${CMAKE_CURRENT_SOURCE_DIR}/../../Middlewares/ST/netxduo/common/src/nx_ip_address_get.c    ${CMAKE_CURRENT_SOURCE_DIR}/../../Middlewares/ST/netxduo/common/src/nx_ip_address_set.c    ${CMAKE_CURRENT_SOURCE_DIR}/../../Middlewares/ST/netxduo/common/src/nx_ip_auxiliary_packet_pool_set.c    ${CMAKE_CURRENT_SOURCE_DIR}/../../Middlewares/ST/netxduo/common/src/nx_ip_checksum_compute.c    ${CMAKE_CURRENT_SOURCE_DIR}/../../Middlewares/ST/netxduo/common/src/nx_ip_create.c    ${CMAKE_CURRENT_SOURCE_DIR}/../../Middlewares/ST/netxduo/common/src/nx_ip_deferred_link_status_process.c    ${CMAKE_CURRENT_SOURCE_DIR}/../../Middlewares/ST/netxduo/common/src/nx_ip_delete.c    ${CMAKE_CURRENT_SOURCE_DIR}/../../Middlewares/ST/netxduo/common/src/nx_ip_delete_queue_clear.c    ${CMAKE_CURRENT_SOURCE_DIR}/../../Middlewares/ST/netxduo/common/src/nx_ip_dispatch_process.c    ${CMAKE_CURRENT_SOURCE_DIR}/../../Middlewares/ST/netxduo/common/src/nx_ip_driver_deferred_enable.c    ${CMAKE_CURRENT_SOURCE_DIR}/../../Middlewares/ST/netxduo/common/src/nx_ip_driver_deferred_processing.c    ${CMAKE_CURRENT_SOURCE_DIR}/../../Middlewares/ST/netxduo/common/src/nx_ip_driver_deferred_receive.c    ${CMAKE_CURRENT_SOURCE_DIR}/../../Middlewares/ST/netxduo/common/src/nx_ip_driver_direct_command.c    ${CMAKE_CURRENT_SOURCE_DIR}/../../Middlewares/ST/netxduo/common/src/nx_ip_driver_interface_direct_command.c    ${CMAKE_CURRENT_SOURCE_DIR}/../../Middlewares/ST/netxduo/common/src/nx_ip_driver_link_status_event.c    ${CMAKE_CURRENT_SOURCE_DIR}/../../Middlewares/ST/netxduo/common/src/nx_ip_driver_packet_send.c    ${CMAKE_CURRENT_SOURCE_DIR}/../../Middlewares/ST/netxduo/common/src/nx_ip_fast_periodic_timer_entry.c    ${CMAKE_CURRENT_SOURCE_DIR}/../../Middlewares/ST/netxduo/common/src/nx_ip_forward_packet_process.c    ${CMAKE_CURRENT_SOURCE_DIR}/../../Middlewares/ST/netxduo/common/src/nx_ip_forwarding_disable.c    ${CMAKE_CURRENT_SOURCE_DIR}/../../Middlewares/ST/netxduo/common/src/nx_ip_forwarding_enable.c    ${CMAKE_CURRENT_SOURCE_DIR}/../../Middlewares/ST/netxduo/common/src/nx_ip_fragment_assembly.c    ${CMAKE_CURRENT_SOURCE_DIR}/../../Middlewares/ST/netxduo/common/src/nx_ip_fragment_disable.c    ${CMAKE_CURRENT_SOURCE_DIR}/../../Middlewares/ST/netxduo/common/src/nx_ip_fragment_enable.c    ${CMAKE_CURRENT_SOURCE_DIR}/../../Middlewares/ST/netxduo/common/src/nx_ip_fragment_forward_packet.c    ${CMAKE_CURRENT_SOURCE_DIR}/../../Middlewares/ST/netxduo/common/src/nx_ip_fragment_packet.c    ${CMAKE_CURRENT_SOURCE_DIR}/../../Middlewares/ST/netxduo/common/src/nx_ip_fragment_timeout_check.c    ${CMAKE_CURRENT_SOURCE_DIR}/../../Middlewares/ST/netxduo/common/src/nx_ip_gateway_address_clear.c    ${CMAKE_CURRENT_SOURCE_DIR}/../../Middlewares/ST/netxduo/common/src/nx_ip_gateway_address_get.c    ${CMAKE_CURRENT_SOURCE_DIR}/../../Middlewares/ST/netxduo/common/src/nx_ip_gateway_address_set.c    ${CMAKE_CURRENT_SOURCE_DIR}/../../Middlewares/ST/netxduo/common/src/nx_ip_header_add.c    ${CMAKE_CURRENT_SOURCE_DIR}/../../Middlewares/ST/netxduo/common/src/nx_ip_info_get.c    ${CMAKE_CURRENT_SOURCE_DIR}/../../Middlewares/ST/netxduo/common/src/nx_ip_initialize.c    ${CMAKE_CURRENT_SOURCE_DIR}/../../Middlewares/ST/netxduo/common/src/nx_ip_interface_address_get.c    ${CMAKE_CURRENT_SOURCE_DIR}/../../Middlewares/ST/netxduo/common/src/nx_ip_interface_address_mapping_configure.c    ${CMAKE_CURRENT_SOURCE_DIR}/../../Middlewares/ST/netxduo/common/src/nx_ip_interface_address_set.c    ${CMAKE_CURRENT_SOURCE_DIR}/../../Middlewares/ST/netxduo/common/src/nx_ip_interface_attach.c    ${CMAKE_CURRENT_SOURCE_DIR}/../../Middlewares/ST/netxduo/common/src/nx_ip_interface_capability_get.c    ${CMAKE_CURRENT_SOURCE_DIR}/../../Middlewares/ST/netxduo/common/src/nx_ip_interface_capability_set.c    ${CMAKE_CURRENT_SOURCE_DIR}/../../Middlewares/ST/netxduo/common/src/nx_ip_interface_detach.c    ${CMAKE_CURRENT_SOURCE_DIR}/../../Middlewares/ST/netxduo/common/src/nx_ip_interface_info_get.c    ${CMAKE_CURRENT_SOURCE_DIR}/../../Middlewares/ST/netxduo/common/src/nx_ip_interface_mtu_set.c    ${CMAKE_CURRENT_SOURCE_DIR}/../../Middlewares/ST/netxduo/common/src/nx_ip_interface_physical_address_get.c    ${CMAKE_CURRENT_SOURCE_DIR}/../../Middlewares/ST/netxduo/common/src/nx_ip_interface_physical_address_set.c    ${CMAKE_CURRENT_SOURCE_DIR}/../../Middlewares/ST/netxduo/common/src/nx_ip_interface_status_check.c    ${CMAKE_CURRENT_SOURCE_DIR}/../../Middlewares/ST/netxduo/common/src/nx_ip_link_status_change_notify_set.c    ${CMAKE_CURRENT_SOURCE_DIR}/../../Middlewares/ST/netxduo/common/src/nx_ip_max_payload_size_find.c    ${CMAKE_CURRENT_SOURCE_DIR}/../../Middlewares/ST/netxduo/common/src/nx_ip_packet_checksum_compute.c    ${CMAKE_CURRENT_SOURCE_DIR}/../../Middlewares/ST/netxduo/common/src/nx_ip_packet_deferred_receive.c    ${CMAKE_CURRENT_SOURCE_DIR}/../../Middlewares/ST/netxduo/common/src/nx_ip_packet_receive.c    ${CMAKE_CURRENT_SOURCE_DIR}/../../Middlewares/ST/netxduo/common/src/nx_ip_packet_send.c    ${CMAKE_CURRENT_SOURCE_DIR}/../../Middlewares/ST/netxduo/common/src/nx_ip_periodic_timer_entry.c    ${CMAKE_CURRENT_SOURCE_DIR}/../../Middlewares/ST/netxduo/common/src/nx_ip_raw_packet_cleanup.c    ${CMAKE_CURRENT_SOURCE_DIR}/../../Middlewares/ST/netxduo/common/src/nx_ip_raw_packet_disable.c    ${CMAKE_CURRENT_SOURCE_DIR}/../../Middlewares/ST/netxduo/common/src/nx_ip_raw_packet_enable.c    ${CMAKE_CURRENT_SOURCE_DIR}/../../Middlewares/ST/netxduo/common/src/nx_ip_raw_packet_filter_set.c    ${CMAKE_CURRENT_SOURCE_DIR}/../../Middlewares/ST/netxduo/common/src/nx_ip_raw_packet_processing.c    ${CMAKE_CURRENT_SOURCE_DIR}/../../Middlewares/ST/netxduo/common/src/nx_ip_raw_packet_receive.c    ${CMAKE_CURRENT_SOURCE_DIR}/../../Middlewares/ST/netxduo/common/src/nx_ip_raw_packet_send.c    ${CMAKE_CURRENT_SOURCE_DIR}/../../Middlewares/ST/netxduo/common/src/nx_ip_raw_packet_source_send.c    ${CMAKE_CURRENT_SOURCE_DIR}/../../Middlewares/ST/netxduo/common/src/nx_ip_raw_receive_queue_max_set.c    ${CMAKE_CURRENT_SOURCE_DIR}/../../Middlewares/ST/netxduo/common/src/nx_ip_route_find.c    ${CMAKE_CURRENT_SOURCE_DIR}/../../Middlewares/ST/netxduo/common/src/nx_ip_static_route_add.c    ${CMAKE_CURRENT_SOURCE_DIR}/../../Middlewares/ST/netxduo/common/src/nx_ip_static_route_delete.c    ${CMAKE_CURRENT_SOURCE_DIR}/../../Middlewares/ST/netxduo/common/src/nx_ip_status_check.c    ${CMAKE_CURRENT_SOURCE_DIR}/../../Middlewares/ST/netxduo/common/src/nx_ip_thread_entry.c    ${CMAKE_CURRENT_SOURCE_DIR}/../../Middlewares/ST/netxduo/common/src/nx_ipv4_multicast_interface_join.c    ${CMAKE_CURRENT_SOURCE_DIR}/../../Middlewares/ST/netxduo/common/src/nx_ipv4_multicast_interface_leave.c    ${CMAKE_CURRENT_SOURCE_DIR}/../../Middlewares/ST/netxduo/common/src/nx_ipv4_option_process.c    ${CMAKE_CURRENT_SOURCE_DIR}/../../Middlewares/ST/netxduo/common/src/nx_ipv4_packet_receive.c    ${CMAKE_CURRENT_SOURCE_DIR}/../../Middlewares/ST/netxduo/common/src/nx_md5.c    ${CMAKE_CURRENT_SOURCE_DIR}/../../Middlewares/ST/netxduo/common/src/nx_packet_allocate.c    ${CMAKE_CURRENT_SOURCE_DIR}/../../Middlewares/ST/netxduo/common/src/nx_packet_copy.c    ${CMAKE_CURRENT_SOURCE_DIR}/../../Middlewares/ST/netxduo/common/src/nx_packet_data_adjust.c    ${CMAKE_CURRENT_SOURCE_DIR}/../../Middlewares/ST/netxduo/common/src/nx_packet_data_append.c    ${CMAKE_CURRENT_SOURCE_DIR}/../../Middlewares/ST/netxduo/common/src/nx_packet_data_extract_offset.c    ${CMAKE_CURRENT_SOURCE_DIR}/../../Middlewares/ST/netxduo/common/src/nx_packet_data_retrieve.c    ${CMAKE_CURRENT_SOURCE_DIR}/../../Middlewares/ST/netxduo/common/src/nx_packet_debug_info_get.c    ${CMAKE_CURRENT_SOURCE_DIR}/../../Middlewares/ST/netxduo/common/src/nx_packet_length_get.c    ${CMAKE_CURRENT_SOURCE_DIR}/../../Middlewares/ST/netxduo/common/src/nx_packet_pool_cleanup.c    ${CMAKE_CURRENT_SOURCE_DIR}/../../Middlewares/ST/netxduo/common/src/nx_packet_pool_create.c    ${CMAKE_CURRENT_SOURCE_DIR}/../../Middlewares/ST/netxduo/common/src/nx_packet_pool_delete.c    ${CMAKE_CURRENT_SOURCE_DIR}/../../Middlewares/ST/netxduo/common/src/nx_packet_pool_info_get.c    ${CMAKE_CURRENT_SOURCE_DIR}/../../Middlewares/ST/netxduo/common/src/nx_packet_pool_initialize.c    ${CMAKE_CURRENT_SOURCE_DIR}/../../Middlewares/ST/netxduo/common/src/nx_packet_pool_low_watermark_set.c    ${CMAKE_CURRENT_SOURCE_DIR}/../../Middlewares/ST/netxduo/common/src/nx_packet_release.c    ${CMAKE_CURRENT_SOURCE_DIR}/../../Middlewares/ST/netxduo/common/src/nx_packet_transmit_release.c    ${CMAKE_CURRENT_SOURCE_DIR}/../../Middlewares/ST/netxduo/common/src/nx_rarp_disable.c    ${CMAKE_CURRENT_SOURCE_DIR}/../../Middlewares/ST/netxduo/common/src/nx_rarp_enable.c    ${CMAKE_CURRENT_SOURCE_DIR}/../../Middlewares/ST/netxduo/common/src/nx_rarp_info_get.c    ${CMAKE_CURRENT_SOURCE_DIR}/../../Middlewares/ST/netxduo/common/src/nx_rarp_packet_deferred_receive.c    ${CMAKE_CURRENT_SOURCE_DIR}/../../Middlewares/ST/netxduo/common/src/nx_rarp_packet_receive.c    ${CMAKE_CURRENT_SOURCE_DIR}/../../Middlewares/ST/netxduo/common/src/nx_rarp_packet_send.c    ${CMAKE_CURRENT_SOURCE_DIR}/../../Middlewares/ST/netxduo/common/src/nx_rarp_periodic_update.c    ${CMAKE_CURRENT_SOURCE_DIR}/../../Middlewares/ST/netxduo/common/src/nx_rarp_queue_process.c    ${CMAKE_CURRENT_SOURCE_DIR}/../../Middlewares/ST/netxduo/common/src/nx_system_initialize.c    ${CMAKE_CURRENT_SOURCE_DIR}/../../Middlewares/ST/netxduo/common/src/nx_tcp_cleanup_deferred.c    ${CMAKE_CURRENT_SOURCE_DIR}/../../Middlewares/ST/netxduo/common/src/nx_tcp_client_bind_cleanup.c    ${CMAKE_CURRENT_SOURCE_DIR}/../../Middlewares/ST/netxduo/common/src/nx_tcp_client_socket_bind.c    ${CMAKE_CURRENT_SOURCE_DIR}/../../Middlewares/ST/netxduo/common/src/nx_tcp_client_socket_connect.c    ${CMAKE_CURRENT_SOURCE_DIR}/../../Middlewares/ST/netxduo/common/src/nx_tcp_client_socket_port_get.c    ${CMAKE_CURRENT_SOURCE_DIR}/../../Middlewares/ST/netxduo/common/src/nx_tcp_client_socket_unbind.c    ${CMAKE_CURRENT_SOURCE_DIR}/../../Middlewares/ST/netxduo/common/src/nx_tcp_connect_cleanup.c    ${CMAKE_CURRENT_SOURCE_DIR}/../../Middlewares/ST/netxduo/common/src/nx_tcp_deferred_cleanup_check.c    ${CMAKE_CURRENT_SOURCE_DIR}/../../Middlewares/ST/netxduo/common/src/nx_tcp_disconnect_cleanup.c    ${CMAKE_CURRENT_SOURCE_DIR}/../../Middlewares/ST/netxduo/common/src/nx_tcp_enable.c    ${CMAKE_CURRENT_SOURCE_DIR}/../../Middlewares/ST/netxduo/common/src/nx_tcp_fast_periodic_processing.c    ${CMAKE_CURRENT_SOURCE_DIR}/../../Middlewares/ST/netxduo/common/src/nx_tcp_free_port_find.c    ${CMAKE_CURRENT_SOURCE_DIR}/../../Middlewares/ST/netxduo/common/src/nx_tcp_info_get.c    ${CMAKE_CURRENT_SOURCE_DIR}/../../Middlewares/ST/netxduo/common/src/nx_tcp_initialize.c    ${CMAKE_CURRENT_SOURCE_DIR}/../../Middlewares/ST/netxduo/common/src/nx_tcp_mss_option_get.c    ${CMAKE_CURRENT_SOURCE_DIR}/../../Middlewares/ST/netxduo/common/src/nx_tcp_no_connection_reset.c    ${CMAKE_CURRENT_SOURCE_DIR}/../../Middlewares/ST/netxduo/common/src/nx_tcp_packet_process.c    ${CMAKE_CURRENT_SOURCE_DIR}/../../Middlewares/ST/netxduo/common/src/nx_tcp_packet_receive.c    ${CMAKE_CURRENT_SOURCE_DIR}/../../Middlewares/ST/netxduo/common/src/nx_tcp_packet_send_ack.c    ${CMAKE_CURRENT_SOURCE_DIR}/../../Middlewares/ST/netxduo/common/src/nx_tcp_packet_send_control.c    ${CMAKE_CURRENT_SOURCE_DIR}/../../Middlewares/ST/netxduo/common/src/nx_tcp_packet_send_fin.c    ${CMAKE_CURRENT_SOURCE_DIR}/../../Middlewares/ST/netxduo/common/src/nx_tcp_packet_send_probe.c    ${CMAKE_CURRENT_SOURCE_DIR}/../../Middlewares/ST/netxduo/common/src/nx_tcp_packet_send_rst.c    ${CMAKE_CURRENT_SOURCE_DIR}/../../Middlewares/ST/netxduo/common/src/nx_tcp_packet_send_syn.c    ${CMAKE_CURRENT_SOURCE_DIR}/../../Middlewares/ST/netxduo/common/src/nx_tcp_periodic_processing.c    ${CMAKE_CURRENT_SOURCE_DIR}/../../Middlewares/ST/netxduo/common/src/nx_tcp_queue_process.c    ${CMAKE_CURRENT_SOURCE_DIR}/../../Middlewares/ST/netxduo/common/src/nx_tcp_receive_cleanup.c    ${CMAKE_CURRENT_SOURCE_DIR}/../../Middlewares/ST/netxduo/common/src/nx_tcp_server_socket_accept.c    ${CMAKE_CURRENT_SOURCE_DIR}/../../Middlewares/ST/netxduo/common/src/nx_tcp_server_socket_listen.c    ${CMAKE_CURRENT_SOURCE_DIR}/../../Middlewares/ST/netxduo/common/src/nx_tcp_server_socket_relisten.c    ${CMAKE_CURRENT_SOURCE_DIR}/../../Middlewares/ST/netxduo/common/src/nx_tcp_server_socket_unaccept.c    ${CMAKE_CURRENT_SOURCE_DIR}/../../Middlewares/ST/netxduo/common/src/nx_tcp_server_socket_unlisten.c    ${CMAKE_CURRENT_SOURCE_DIR}/../../Middlewares/ST/netxduo/common/src/nx_tcp_socket_block_cleanup.c    ${CMAKE_CURRENT_SOURCE_DIR}/../../Middlewares/ST/netxduo/common/src/nx_tcp_socket_bytes_available.c    ${CMAKE_CURRENT_SOURCE_DIR}/../../Middlewares/ST/netxduo/common/src/nx_tcp_socket_connection_reset.c    ${CMAKE_CURRENT_SOURCE_DIR}/../../Middlewares/ST/netxduo/common/src/nx_tcp_socket_create.c    ${CMAKE_CURRENT_SOURCE_DIR}/../../Middlewares/ST/netxduo/common/src/nx_tcp_socket_delete.c    ${CMAKE_CURRENT_SOURCE_DIR}/../../Middlewares/ST/netxduo/common/src/nx_tcp_socket_disconnect.c    ${CMAKE_CURRENT_SOURCE_DIR}/../../Middlewares/ST/netxduo/common/src/nx_tcp_socket_disconnect_complete_notify.c    ${CMAKE_CURRENT_SOURCE_DIR}/../../Middlewares/ST/netxduo/common/src/nx_tcp_socket_establish_notify.c    ${CMAKE_CURRENT_SOURCE_DIR}/../../Middlewares/ST/netxduo/common/src/nx_tcp_socket_info_get.c    ${CMAKE_CURRENT_SOURCE_DIR}/../../Middlewares/ST/netxduo/common/src/nx_tcp_socket_mss_get.c    ${CMAKE_CURRENT_SOURCE_DIR}/../../Middlewares/ST/netxduo/common/src/nx_tcp_socket_mss_peer_get.c    ${CMAKE_CURRENT_SOURCE_DIR}/../../Middlewares/ST/netxduo/common/src/nx_tcp_socket_mss_set.c    ${CMAKE_CURRENT_SOURCE_DIR}/../../Middlewares/ST/netxduo/common/src/nx_tcp_socket_packet_process.c    ${CMAKE_CURRENT_SOURCE_DIR}/../../Middlewares/ST/netxduo/common/src/nx_tcp_socket_peer_info_get.c    ${CMAKE_CURRENT_SOURCE_DIR}/../../Middlewares/ST/netxduo/common/src/nx_tcp_socket_queue_depth_notify_set.c    ${CMAKE_CURRENT_SOURCE_DIR}/../../Middlewares/ST/netxduo/common/src/nx_tcp_socket_receive.c    ${CMAKE_CURRENT_SOURCE_DIR}/../../Middlewares/ST/netxduo/common/src/nx_tcp_socket_receive_notify.c    ${CMAKE_CURRENT_SOURCE_DIR}/../../Middlewares/ST/netxduo/common/src/nx_tcp_socket_receive_queue_flush.c    ${CMAKE_CURRENT_SOURCE_DIR}/../../Middlewares/ST/netxduo/common/src/nx_tcp_socket_receive_queue_max_set.c    ${CMAKE_CURRENT_SOURCE_DIR}/../../Middlewares/ST/netxduo/common/src/nx_tcp_socket_retransmit.c    ${CMAKE_CURRENT_SOURCE_DIR}/../../Middlewares/ST/netxduo/common/src/nx_tcp_socket_send.c    ${CMAKE_CURRENT_SOURCE_DIR}/../../Middlewares/ST/netxduo/common/src/nx_tcp_socket_send_internal.c    ${CMAKE_CURRENT_SOURCE_DIR}/../../Middlewares/ST/netxduo/common/src/nx_tcp_socket_state_ack_check.c    ${CMAKE_CURRENT_SOURCE_DIR}/../../Middlewares/ST/netxduo/common/src/nx_tcp_socket_state_closing.c    ${CMAKE_CURRENT_SOURCE_DIR}/../../Middlewares/ST/netxduo/common/src/nx_tcp_socket_state_data_check.c    ${CMAKE_CURRENT_SOURCE_DIR}/../../Middlewares/ST/netxduo/common/src/nx_tcp_socket_state_established.c    ${CMAKE_CURRENT_SOURCE_DIR}/../../Middlewares/ST/netxduo/common/src/nx_tcp_socket_state_fin_wait1.c    ${CMAKE_CURRENT_SOURCE_DIR}/../../Middlewares/ST/netxduo/common/src/nx_tcp_socket_state_fin_wait2.c    ${CMAKE_CURRENT_SOURCE_DIR}/../../Middlewares/ST/netxduo/common/src/nx_tcp_socket_state_last_ack.c    ${CMAKE_CURRENT_SOURCE_DIR}/../../Middlewares/ST/netxduo/common/src/nx_tcp_socket_state_syn_received.c    ${CMAKE_CURRENT_SOURCE_DIR}/../../Middlewares/ST/netxduo/common/src/nx_tcp_socket_state_syn_sent.c    ${CMAKE_CURRENT_SOURCE_DIR}/../../Middlewares/ST/netxduo/common/src/nx_tcp_socket_state_transmit_check.c    ${CMAKE_CURRENT_SOURCE_DIR}/../../Middlewares/ST/netxduo/common/src/nx_tcp_socket_state_wait.c    ${CMAKE_CURRENT_SOURCE_DIR}/../../Middlewares/ST/netxduo/common/src/nx_tcp_socket_thread_resume.c    ${CMAKE_CURRENT_SOURCE_DIR}/../../Middlewares/ST/netxduo/common/src/nx_tcp_socket_thread_suspend.c    ${CMAKE_CURRENT_SOURCE_DIR}/../../Middlewares/ST/netxduo/common/src/nx_tcp_socket_timed_wait_callback.c    ${CMAKE_CURRENT_SOURCE_DIR}/../../Middlewares/ST/netxduo/common/src/nx_tcp_socket_transmit_configure.c    ${CMAKE_CURRENT_SOURCE_DIR}/../../Middlewares/ST/netxduo/common/src/nx_tcp_socket_transmit_queue_flush.c    ${CMAKE_CURRENT_SOURCE_DIR}/../../Middlewares/ST/netxduo/common/src/nx_tcp_socket_window_update_notify_set.c    ${CMAKE_CURRENT_SOURCE_DIR}/../../Middlewares/ST/netxduo/common/src/nx_tcp_transmit_cleanup.c    ${CMAKE_CURRENT_SOURCE_DIR}/../../Middlewares/ST/netxduo/common/src/nx_tcp_window_scaling_option_get.c    ${CMAKE_CURRENT_SOURCE_DIR}/../../Middlewares/ST/netxduo/common/src/nx_udp_bind_cleanup.c    ${CMAKE_CURRENT_SOURCE_DIR}/../../Middlewares/ST/netxduo/common/src/nx_udp_enable.c    ${CMAKE_CURRENT_SOURCE_DIR}/../../Middlewares/ST/netxduo/common/src/nx_udp_free_port_find.c    ${CMAKE_CURRENT_SOURCE_DIR}/../../Middlewares/ST/netxduo/common/src/nx_udp_info_get.c    ${CMAKE_CURRENT_SOURCE_DIR}/../../Middlewares/ST/netxduo/common/src/nx_udp_packet_info_extract.c    ${CMAKE_CURRENT_SOURCE_DIR}/../../Middlewares/ST/netxduo/common/src/nx_udp_packet_receive.c    ${CMAKE_CURRENT_SOURCE_DIR}/../../Middlewares/ST/netxduo/common/src/nx_udp_receive_cleanup.c    ${CMAKE_CURRENT_SOURCE_DIR}/../../Middlewares/ST/netxduo/common/src/nx_udp_socket_bind.c    ${CMAKE_CURRENT_SOURCE_DIR}/../../Middlewares/ST/netxduo/common/src/nx_udp_socket_bytes_available.c    ${CMAKE_CURRENT_SOURCE_DIR}/../../Middlewares/ST/netxduo/common/src/nx_udp_socket_checksum_disable.c    ${CMAKE_CURRENT_SOURCE_DIR}/../../Middlewares/ST/netxduo/common/src/nx_udp_socket_checksum_enable.c    ${CMAKE_CURRENT_SOURCE_DIR}/../../Middlewares/ST/netxduo/common/src/nx_udp_socket_create.c    ${CMAKE_CURRENT_SOURCE_DIR}/../../Middlewares/ST/netxduo/common/src/nx_udp_socket_delete.c    ${CMAKE_CURRENT_SOURCE_DIR}/../../Middlewares/ST/netxduo/common/src/nx_udp_socket_info_get.c    ${CMAKE_CURRENT_SOURCE_DIR}/../../Middlewares/ST/netxduo/common/src/nx_udp_socket_port_get.c    ${CMAKE_CURRENT_SOURCE_DIR}/../../Middlewares/ST/netxduo/common/src/nx_udp_socket_receive.c    ${CMAKE_CURRENT_SOURCE_DIR}/../../Middlewares/ST/netxduo/common/src/nx_udp_socket_receive_notify.c    ${CMAKE_CURRENT_SOURCE_DIR}/../../Middlewares/ST/netxduo/common/src/nx_udp_socket_send.c    ${CMAKE_CURRENT_SOURCE_DIR}/../../Middlewares/ST/netxduo/common/src/nx_udp_socket_source_send.c    ${CMAKE_CURRENT_SOURCE_DIR}/../../Middlewares/ST/netxduo/common/src/nx_udp_socket_unbind.c    ${CMAKE_CURRENT_SOURCE_DIR}/../../Middlewares/ST/netxduo/common/src/nx_udp_source_extract.c    ${CMAKE_CURRENT_SOURCE_DIR}/../../Middlewares/ST/netxduo/common/src/nx_utility.c    ${CMAKE_CURRENT_SOURCE_DIR}/../../Middlewares/ST/netxduo/common/src/nxd_icmp_enable.c    ${CMAKE_CURRENT_SOURCE_DIR}/../../Middlewares/ST/netxduo/common/src/nxd_icmp_ping.c    ${CMAKE_CURRENT_SOURCE_DIR}/../../Middlewares/ST/netxduo/common/src/nxd_icmp_source_ping.c    ${CMAKE_CURRENT_SOURCE_DIR}/../../Middlewares/ST/netxduo/common/src/nxd_ip_raw_packet_send.c    ${CMAKE_CURRENT_SOURCE_DIR}/../../Middlewares/ST/netxduo/common/src/nxd_ip_raw_packet_source_send.c    ${CMAKE_CURRENT_SOURCE_DIR}/../../Middlewares/ST/netxduo/common/src/nxd_tcp_client_socket_connect.c    ${CMAKE_CURRENT_SOURCE_DIR}/../../Middlewares/ST/netxduo/common/src/nxd_tcp_socket_peer_info_get.c    ${CMAKE_CURRENT_SOURCE_DIR}/../../Middlewares/ST/netxduo/common/src/nxd_udp_packet_info_extract.c    ${CMAKE_CURRENT_SOURCE_DIR}/../../Middlewares/ST/netxduo/common/src/nxd_udp_socket_send.c    ${CMAKE_CURRENT_SOURCE_DIR}/../../Middlewares/ST/netxduo/common/src/nxd_udp_socket_source_send.c    ${CMAKE_CURRENT_SOURCE_DIR}/../../Middlewares/ST/netxduo/common/src/nxd_udp_source_extract.c    ${CMAKE_CURRENT_SOURCE_DIR}/../../Middlewares/ST/netxduo/common/src/nxde_icmp_enable.c    ${CMAKE_CURRENT_SOURCE_DIR}/../../Middlewares/ST/netxduo/common/src/nxde_icmp_ping.c    ${CMAKE_CURRENT_SOURCE_DIR}/../../Middlewares/ST/netxduo/common/src/nxde_icmp_source_ping.c    ${CMAKE_CURRENT_SOURCE_DIR}/../../Middlewares/ST/netxduo/common/src/nxde_ip_raw_packet_send.c    ${CMAKE_CURRENT_SOURCE_DIR}/../../Middlewares/ST/netxduo/common/src/nxde_ip_raw_packet_source_send.c    ${CMAKE_CURRENT_SOURCE_DIR}/../../Middlewares/ST/netxduo/common/src/nxde_tcp_client_socket_connect.c    ${CMAKE_CURRENT_SOURCE_DIR}/../../Middlewares/ST/netxduo/common/src/nxde_tcp_socket_peer_info_get.c    ${CMAKE_CURRENT_SOURCE_DIR}/../../Middlewares/ST/netxduo/common/src/nxde_udp_packet_info_extract.c    ${CMAKE_CURRENT_SOURCE_DIR}/../../Middlewares/ST/netxduo/common/src/nxde_udp_socket_send.c    ${CMAKE_CURRENT_SOURCE_DIR}/../../Middlewares/ST/netxduo/common/src/nxde_udp_socket_source_send.c    ${CMAKE_CURRENT_SOURCE_DIR}/../../Middlewares/ST/netxduo/common/src/nxde_udp_source_extract.c    ${CMAKE_CURRENT_SOURCE_DIR}/../../Middlewares/ST/netxduo/common/src/nxe_arp_dynamic_entries_invalidate.c    ${CMAKE_CURRENT_SOURCE_DIR}/../../Middlewares/ST/netxduo/common/src/nxe_arp_dynamic_entry_set.c    ${CMAKE_CURRENT_SOURCE_DIR}/../../Middlewares/ST/netxduo/common/src/nxe_arp_enable.c    ${CMAKE_CURRENT_SOURCE_DIR}/../../Middlewares/ST/netxduo/common/src/nxe_arp_entry_delete.c    ${CMAKE_CURRENT_SOURCE_DIR}/../../Middlewares/ST/netxduo/common/src/nxe_arp_gratuitous_send.c    ${CMAKE_CURRENT_SOURCE_DIR}/../../Middlewares/ST/netxduo/common/src/nxe_arp_hardware_address_find.c    ${CMAKE_CURRENT_SOURCE_DIR}/../../Middlewares/ST/netxduo/common/src/nxe_arp_info_get.c    ${CMAKE_CURRENT_SOURCE_DIR}/../../Middlewares/ST/netxduo/common/src/nxe_arp_ip_address_find.c    ${CMAKE_CURRENT_SOURCE_DIR}/../../Middlewares/ST/netxduo/common/src/nxe_arp_static_entries_delete.c    ${CMAKE_CURRENT_SOURCE_DIR}/../../Middlewares/ST/netxduo/common/src/nxe_arp_static_entry_create.c    ${CMAKE_CURRENT_SOURCE_DIR}/../../Middlewares/ST/netxduo/common/src/nxe_arp_static_entry_delete.c    ${CMAKE_CURRENT_SOURCE_DIR}/../../Middlewares/ST/netxduo/common/src/nxe_icmp_enable.c    ${CMAKE_CURRENT_SOURCE_DIR}/../../Middlewares/ST/netxduo/common/src/nxe_icmp_info_get.c    ${CMAKE_CURRENT_SOURCE_DIR}/../../Middlewares/ST/netxduo/common/src/nxe_icmp_ping.c    ${CMAKE_CURRENT_SOURCE_DIR}/../../Middlewares/ST/netxduo/common/src/nxe_igmp_enable.c    ${CMAKE_CURRENT_SOURCE_DIR}/../../Middlewares/ST/netxduo/common/src/nxe_igmp_info_get.c    ${CMAKE_CURRENT_SOURCE_DIR}/../../Middlewares/ST/netxduo/common/src/nxe_igmp_loopback_disable.c    ${CMAKE_CURRENT_SOURCE_DIR}/../../Middlewares/ST/netxduo/common/src/nxe_igmp_loopback_enable.c    ${CMAKE_CURRENT_SOURCE_DIR}/../../Middlewares/ST/netxduo/common/src/nxe_igmp_multicast_interface_join.c    ${CMAKE_CURRENT_SOURCE_DIR}/../../Middlewares/ST/netxduo/common/src/nxe_igmp_multicast_interface_leave.c    ${CMAKE_CURRENT_SOURCE_DIR}/../../Middlewares/ST/netxduo/common/src/nxe_igmp_multicast_join.c    ${CMAKE_CURRENT_SOURCE_DIR}/../../Middlewares/ST/netxduo/common/src/nxe_igmp_multicast_leave.c    ${CMAKE_CURRENT_SOURCE_DIR}/../../Middlewares/ST/netxduo/common/src/nxe_ip_address_change_notify.c    ${CMAKE_CURRENT_SOURCE_DIR}/../../Middlewares/ST/netxduo/common/src/nxe_ip_address_get.c    ${CMAKE_CURRENT_SOURCE_DIR}/../../Middlewares/ST/netxduo/common/src/nxe_ip_address_set.c    ${CMAKE_CURRENT_SOURCE_DIR}/../../Middlewares/ST/netxduo/common/src/nxe_ip_auxiliary_packet_pool_set.c    ${CMAKE_CURRENT_SOURCE_DIR}/../../Middlewares/ST/netxduo/common/src/nxe_ip_create.c    ${CMAKE_CURRENT_SOURCE_DIR}/../../Middlewares/ST/netxduo/common/src/nxe_ip_delete.c    ${CMAKE_CURRENT_SOURCE_DIR}/../../Middlewares/ST/netxduo/common/src/nxe_ip_driver_direct_command.c    ${CMAKE_CURRENT_SOURCE_DIR}/../../Middlewares/ST/netxduo/common/src/nxe_ip_driver_interface_direct_command.c    ${CMAKE_CURRENT_SOURCE_DIR}/../../Middlewares/ST/netxduo/common/src/nxe_ip_forwarding_disable.c    ${CMAKE_CURRENT_SOURCE_DIR}/../../Middlewares/ST/netxduo/common/src/nxe_ip_forwarding_enable.c    ${CMAKE_CURRENT_SOURCE_DIR}/../../Middlewares/ST/netxduo/common/src/nxe_ip_fragment_disable.c    ${CMAKE_CURRENT_SOURCE_DIR}/../../Middlewares/ST/netxduo/common/src/nxe_ip_fragment_enable.c    ${CMAKE_CURRENT_SOURCE_DIR}/../../Middlewares/ST/netxduo/common/src/nxe_ip_gateway_address_clear.c    ${CMAKE_CURRENT_SOURCE_DIR}/../../Middlewares/ST/netxduo/common/src/nxe_ip_gateway_address_get.c    ${CMAKE_CURRENT_SOURCE_DIR}/../../Middlewares/ST/netxduo/common/src/nxe_ip_gateway_address_set.c    ${CMAKE_CURRENT_SOURCE_DIR}/../../Middlewares/ST/netxduo/common/src/nxe_ip_info_get.c    ${CMAKE_CURRENT_SOURCE_DIR}/../../Middlewares/ST/netxduo/common/src/nxe_ip_interface_address_get.c    ${CMAKE_CURRENT_SOURCE_DIR}/../../Middlewares/ST/netxduo/common/src/nxe_ip_interface_address_mapping_configure.c    ${CMAKE_CURRENT_SOURCE_DIR}/../../Middlewares/ST/netxduo/common/src/nxe_ip_interface_address_set.c    ${CMAKE_CURRENT_SOURCE_DIR}/../../Middlewares/ST/netxduo/common/src/nxe_ip_interface_attach.c    ${CMAKE_CURRENT_SOURCE_DIR}/../../Middlewares/ST/netxduo/common/src/nxe_ip_interface_capability_get.c    ${CMAKE_CURRENT_SOURCE_DIR}/../../Middlewares/ST/netxduo/common/src/nxe_ip_interface_capability_set.c    ${CMAKE_CURRENT_SOURCE_DIR}/../../Middlewares/ST/netxduo/common/src/nxe_ip_interface_detach.c    ${CMAKE_CURRENT_SOURCE_DIR}/../../Middlewares/ST/netxduo/common/src/nxe_ip_interface_info_get.c    ${CMAKE_CURRENT_SOURCE_DIR}/../../Middlewares/ST/netxduo/common/src/nxe_ip_interface_mtu_set.c    ${CMAKE_CURRENT_SOURCE_DIR}/../../Middlewares/ST/netxduo/common/src/nxe_ip_interface_physical_address_get.c    ${CMAKE_CURRENT_SOURCE_DIR}/../../Middlewares/ST/netxduo/common/src/nxe_ip_interface_physical_address_set.c    ${CMAKE_CURRENT_SOURCE_DIR}/../../Middlewares/ST/netxduo/common/src/nxe_ip_interface_status_check.c    ${CMAKE_CURRENT_SOURCE_DIR}/../../Middlewares/ST/netxduo/common/src/nxe_ip_link_status_change_notify_set.c    ${CMAKE_CURRENT_SOURCE_DIR}/../../Middlewares/ST/netxduo/common/src/nxe_ip_max_payload_size_find.c    ${CMAKE_CURRENT_SOURCE_DIR}/../../Middlewares/ST/netxduo/common/src/nxe_ip_raw_packet_disable.c    ${CMAKE_CURRENT_SOURCE_DIR}/../../Middlewares/ST/netxduo/common/src/nxe_ip_raw_packet_enable.c    ${CMAKE_CURRENT_SOURCE_DIR}/../../Middlewares/ST/netxduo/common/src/nxe_ip_raw_packet_filter_set.c    ${CMAKE_CURRENT_SOURCE_DIR}/../../Middlewares/ST/netxduo/common/src/nxe_ip_raw_packet_receive.c    ${CMAKE_CURRENT_SOURCE_DIR}/../../Middlewares/ST/netxduo/common/src/nxe_ip_raw_packet_send.c    ${CMAKE_CURRENT_SOURCE_DIR}/../../Middlewares/ST/netxduo/common/src/nxe_ip_raw_packet_source_send.c    ${CMAKE_CURRENT_SOURCE_DIR}/../../Middlewares/ST/netxduo/common/src/nxe_ip_raw_receive_queue_max_set.c    ${CMAKE_CURRENT_SOURCE_DIR}/../../Middlewares/ST/netxduo/common/src/nxe_ip_static_route_add.c    ${CMAKE_CURRENT_SOURCE_DIR}/../../Middlewares/ST/netxduo/common/src/nxe_ip_static_route_delete.c    ${CMAKE_CURRENT_SOURCE_DIR}/../../Middlewares/ST/netxduo/common/src/nxe_ip_status_check.c    ${CMAKE_CURRENT_SOURCE_DIR}/../../Middlewares/ST/netxduo/common/src/nxe_ipv4_multicast_interface_join.c    ${CMAKE_CURRENT_SOURCE_DIR}/../../Middlewares/ST/netxduo/common/src/nxe_ipv4_multicast_interface_leave.c    ${CMAKE_CURRENT_SOURCE_DIR}/../../Middlewares/ST/netxduo/common/src/nxe_packet_allocate.c    ${CMAKE_CURRENT_SOURCE_DIR}/../../Middlewares/ST/netxduo/common/src/nxe_packet_copy.c    ${CMAKE_CURRENT_SOURCE_DIR}/../../Middlewares/ST/netxduo/common/src/nxe_packet_data_append.c    ${CMAKE_CURRENT_SOURCE_DIR}/../../Middlewares/ST/netxduo/common/src/nxe_packet_data_extract_offset.c    ${CMAKE_CURRENT_SOURCE_DIR}/../../Middlewares/ST/netxduo/common/src/nxe_packet_data_retrieve.c    ${CMAKE_CURRENT_SOURCE_DIR}/../../Middlewares/ST/netxduo/common/src/nxe_packet_length_get.c    ${CMAKE_CURRENT_SOURCE_DIR}/../../Middlewares/ST/netxduo/common/src/nxe_packet_pool_create.c    ${CMAKE_CURRENT_SOURCE_DIR}/../../Middlewares/ST/netxduo/common/src/nxe_packet_pool_delete.c    ${CMAKE_CURRENT_SOURCE_DIR}/../../Middlewares/ST/netxduo/common/src/nxe_packet_pool_info_get.c    ${CMAKE_CURRENT_SOURCE_DIR}/../../Middlewares/ST/netxduo/common/src/nxe_packet_pool_low_watermark_set.c    ${CMAKE_CURRENT_SOURCE_DIR}/../../Middlewares/ST/netxduo/common/src/nxe_packet_release.c    ${CMAKE_CURRENT_SOURCE_DIR}/../../Middlewares/ST/netxduo/common/src/nxe_packet_transmit_release.c    ${CMAKE_CURRENT_SOURCE_DIR}/../../Middlewares/ST/netxduo/common/src/nxe_rarp_disable.c    ${CMAKE_CURRENT_SOURCE_DIR}/../../Middlewares/ST/netxduo/common/src/nxe_rarp_enable.c    ${CMAKE_CURRENT_SOURCE_DIR}/../../Middlewares/ST/netxduo/common/src/nxe_rarp_info_get.c    ${CMAKE_CURRENT_SOURCE_DIR}/../../Middlewares/ST/netxduo/common/src/nxe_tcp_client_socket_bind.c    ${CMAKE_CURRENT_SOURCE_DIR}/../../Middlewares/ST/netxduo/common/src/nxe_tcp_client_socket_connect.c    ${CMAKE_CURRENT_SOURCE_DIR}/../../Middlewares/ST/netxduo/common/src/nxe_tcp_client_socket_port_get.c    ${CMAKE_CURRENT_SOURCE_DIR}/../../Middlewares/ST/netxduo/common/src/nxe_tcp_client_socket_unbind.c    ${CMAKE_CURRENT_SOURCE_DIR}/../../Middlewares/ST/netxduo/common/src/nxe_tcp_enable.c    ${CMAKE_CURRENT_SOURCE_DIR}/../../Middlewares/ST/netxduo/common/src/nxe_tcp_free_port_find.c    ${CMAKE_CURRENT_SOURCE_DIR}/../../Middlewares/ST/netxduo/common/src/nxe_tcp_info_get.c    ${CMAKE_CURRENT_SOURCE_DIR}/../../Middlewares/ST/netxduo/common/src/nxe_tcp_server_socket_accept.c    ${CMAKE_CURRENT_SOURCE_DIR}/../../Middlewares/ST/netxduo/common/src/nxe_tcp_server_socket_listen.c    ${CMAKE_CURRENT_SOURCE_DIR}/../../Middlewares/ST/netxduo/common/src/nxe_tcp_server_socket_relisten.c    ${CMAKE_CURRENT_SOURCE_DIR}/../../Middlewares/ST/netxduo/common/src/nxe_tcp_server_socket_unaccept.c    ${CMAKE_CURRENT_SOURCE_DIR}/../../Middlewares/ST/netxduo/common/src/nxe_tcp_server_socket_unlisten.c    ${CMAKE_CURRENT_SOURCE_DIR}/../../Middlewares/ST/netxduo/common/src/nxe_tcp_socket_bytes_available.c    ${CMAKE_CURRENT_SOURCE_DIR}/../../Middlewares/ST/netxduo/common/src/nxe_tcp_socket_create.c    ${CMAKE_CURRENT_SOURCE_DIR}/../../Middlewares/ST/netxduo/common/src/nxe_tcp_socket_delete.c    ${CMAKE_CURRENT_SOURCE_DIR}/../../Middlewares/ST/netxduo/common/src/nxe_tcp_socket_disconnect.c    ${CMAKE_CURRENT_SOURCE_DIR}/../../Middlewares/ST/netxduo/common/src/nxe_tcp_socket_disconnect_complete_notify.c    ${CMAKE_CURRENT_SOURCE_DIR}/../../Middlewares/ST/netxduo/common/src/nxe_tcp_socket_establish_notify.c    ${CMAKE_CURRENT_SOURCE_DIR}/../../Middlewares/ST/netxduo/common/src/nxe_tcp_socket_info_get.c    ${CMAKE_CURRENT_SOURCE_DIR}/../../Middlewares/ST/netxduo/common/src/nxe_tcp_socket_mss_get.c    ${CMAKE_CURRENT_SOURCE_DIR}/../../Middlewares/ST/netxduo/common/src/nxe_tcp_socket_mss_peer_get.c    ${CMAKE_CURRENT_SOURCE_DIR}/../../Middlewares/ST/netxduo/common/src/nxe_tcp_socket_mss_set.c    ${CMAKE_CURRENT_SOURCE_DIR}/../../Middlewares/ST/netxduo/common/src/nxe_tcp_socket_peer_info_get.c    ${CMAKE_CURRENT_SOURCE_DIR}/../../Middlewares/ST/netxduo/common/src/nxe_tcp_socket_queue_depth_notify_set.c    ${CMAKE_CURRENT_SOURCE_DIR}/../../Middlewares/ST/netxduo/common/src/nxe_tcp_socket_receive.c    ${CMAKE_CURRENT_SOURCE_DIR}/../../Middlewares/ST/netxduo/common/src/nxe_tcp_socket_receive_notify.c    ${CMAKE_CURRENT_SOURCE_DIR}/../../Middlewares/ST/netxduo/common/src/nxe_tcp_socket_receive_queue_max_set.c    ${CMAKE_CURRENT_SOURCE_DIR}/../../Middlewares/ST/netxduo/common/src/nxe_tcp_socket_send.c    ${CMAKE_CURRENT_SOURCE_DIR}/../../Middlewares/ST/netxduo/common/src/nxe_tcp_socket_state_wait.c    ${CMAKE_CURRENT_SOURCE_DIR}/../../Middlewares/ST/netxduo/common/src/nxe_tcp_socket_timed_wait_callback.c    ${CMAKE_CURRENT_SOURCE_DIR}/../../Middlewares/ST/netxduo/common/src/nxe_tcp_socket_transmit_configure.c    ${CMAKE_CURRENT_SOURCE_DIR}/../../Middlewares/ST/netxduo/common/src/nxe_tcp_socket_window_update_notify_set.c    ${CMAKE_CURRENT_SOURCE_DIR}/../../Middlewares/ST/netxduo/common/src/nxe_udp_enable.c    ${CMAKE_CURRENT_SOURCE_DIR}/../../Middlewares/ST/netxduo/common/src/nxe_udp_free_port_find.c    ${CMAKE_CURRENT_SOURCE_DIR}/../../Middlewares/ST/netxduo/common/src/nxe_udp_info_get.c    ${CMAKE_CURRENT_SOURCE_DIR}/../../Middlewares/ST/netxduo/common/src/nxe_udp_packet_info_extract.c    ${CMAKE_CURRENT_SOURCE_DIR}/../../Middlewares/ST/netxduo/common/src/nxe_udp_socket_bind.c    ${CMAKE_CURRENT_SOURCE_DIR}/../../Middlewares/ST/netxduo/common/src/nxe_udp_socket_bytes_available.c    ${CMAKE_CURRENT_SOURCE_DIR}/../../Middlewares/ST/netxduo/common/src/nxe_udp_socket_checksum_disable.c    ${CMAKE_CURRENT_SOURCE_DIR}/../../Middlewares/ST/netxduo/common/src/nxe_udp_socket_checksum_enable.c    ${CMAKE_CURRENT_SOURCE_DIR}/../../Middlewares/ST/netxduo/common/src/nxe_udp_socket_create.c    ${CMAKE_CURRENT_SOURCE_DIR}/../../Middlewares/ST/netxduo/common/src/nxe_udp_socket_delete.c    ${CMAKE_CURRENT_SOURCE_DIR}/../../Middlewares/ST/netxduo/common/src/nxe_udp_socket_info_get.c    ${CMAKE_CURRENT_SOURCE_DIR}/../../Middlewares/ST/netxduo/common/src/nxe_udp_socket_port_get.c    ${CMAKE_CURRENT_SOURCE_DIR}/../../Middlewares/ST/netxduo/common/src/nxe_udp_socket_receive.c    ${CMAKE_CURRENT_SOURCE_DIR}/../../Middlewares/ST/netxduo/common/src/nxe_udp_socket_receive_notify.c    ${CMAKE_CURRENT_SOURCE_DIR}/../../Middlewares/ST/netxduo/common/src/nxe_udp_socket_send.c    ${CMAKE_CURRENT_SOURCE_DIR}/../../Middlewares/ST/netxduo/common/src/nxe_udp_socket_source_send.c    ${CMAKE_CURRENT_SOURCE_DIR}/../../Middlewares/ST/netxduo/common/src/nxe_udp_socket_unbind.c    ${CMAKE_CURRENT_SOURCE_DIR}/../../Middlewares/ST/netxduo/common/src/nxe_udp_socket_vlan_priority_set.c    ${CMAKE_CURRENT_SOURCE_DIR}/../../Middlewares/ST/netxduo/common/src/nxe_tcp_socket_vlan_priority_set.c    ${CMAKE_CURRENT_SOURCE_DIR}/../../Middlewares/ST/netxduo/common/src/nxe_packet_vlan_priority_set.c    ${CMAKE_CURRENT_SOURCE_DIR}/../../Middlewares/ST/netxduo/common/src/nx_udp_socket_vlan_priority_set.c    ${CMAKE_CURRENT_SOURCE_DIR}/../../Middlewares/ST/netxduo/common/src/nx_tcp_socket_vlan_priority_set.c    ${CMAKE_CURRENT_SOURCE_DIR}/../../Middlewares/ST/netxduo/common/src/nx_packet_vlan_priority_set.c    ${CMAKE_CURRENT_SOURCE_DIR}/../../Middlewares/ST/netxduo/common/src/nxe_udp_source_extract.c    ${CMAKE_CURRENT_SOURCE_DIR}/../../Middlewares/ST/netxduo/common/src/nx_icmp_ping6.c    ${CMAKE_CURRENT_SOURCE_DIR}/../../Middlewares/ST/netxduo/common/src/nx_icmpv6_DAD_clear_NDCache_entry.c    ${CMAKE_CURRENT_SOURCE_DIR}/../../Middlewares/ST/netxduo/common/src/nx_icmpv6_DAD_failure.c    ${CMAKE_CURRENT_SOURCE_DIR}/../../Middlewares/ST/netxduo/common/src/nx_icmpv6_dest_table_add.c    ${CMAKE_CURRENT_SOURCE_DIR}/../../Middlewares/ST/netxduo/common/src/nx_icmpv6_dest_table_find.c    ${CMAKE_CURRENT_SOURCE_DIR}/../../Middlewares/ST/netxduo/common/src/nx_icmpv6_destination_table_periodic_update.c    ${CMAKE_CURRENT_SOURCE_DIR}/../../Middlewares/ST/netxduo/common/src/nx_icmpv6_packet_process.c    ${CMAKE_CURRENT_SOURCE_DIR}/../../Middlewares/ST/netxduo/common/src/nx_icmpv6_perform_DAD.c    ${CMAKE_CURRENT_SOURCE_DIR}/../../Middlewares/ST/netxduo/common/src/nx_icmpv6_process_echo_reply.c    ${CMAKE_CURRENT_SOURCE_DIR}/../../Middlewares/ST/netxduo/common/src/nx_icmpv6_process_echo_request.c    ${CMAKE_CURRENT_SOURCE_DIR}/../../Middlewares/ST/netxduo/common/src/nx_icmpv6_process_na.c    ${CMAKE_CURRENT_SOURCE_DIR}/../../Middlewares/ST/netxduo/common/src/nx_icmpv6_process_ns.c    ${CMAKE_CURRENT_SOURCE_DIR}/../../Middlewares/ST/netxduo/common/src/nx_icmpv6_process_packet_too_big.c    ${CMAKE_CURRENT_SOURCE_DIR}/../../Middlewares/ST/netxduo/common/src/nx_icmpv6_process_ra.c    ${CMAKE_CURRENT_SOURCE_DIR}/../../Middlewares/ST/netxduo/common/src/nx_icmpv6_process_redirect.c    ${CMAKE_CURRENT_SOURCE_DIR}/../../Middlewares/ST/netxduo/common/src/nx_icmpv6_send_error_message.c    ${CMAKE_CURRENT_SOURCE_DIR}/../../Middlewares/ST/netxduo/common/src/nx_icmpv6_send_ns.c    ${CMAKE_CURRENT_SOURCE_DIR}/../../Middlewares/ST/netxduo/common/src/nx_icmpv6_send_queued_packets.c    ${CMAKE_CURRENT_SOURCE_DIR}/../../Middlewares/ST/netxduo/common/src/nx_icmpv6_send_rs.c    ${CMAKE_CURRENT_SOURCE_DIR}/../../Middlewares/ST/netxduo/common/src/nx_icmpv6_validate_neighbor_message.c    ${CMAKE_CURRENT_SOURCE_DIR}/../../Middlewares/ST/netxduo/common/src/nx_icmpv6_validate_options.c    ${CMAKE_CURRENT_SOURCE_DIR}/../../Middlewares/ST/netxduo/common/src/nx_icmpv6_validate_ra.c    ${CMAKE_CURRENT_SOURCE_DIR}/../../Middlewares/ST/netxduo/common/src/nx_ipv6_fragment_process.c    ${CMAKE_CURRENT_SOURCE_DIR}/../../Middlewares/ST/netxduo/common/src/nx_ipv6_header_add.c    ${CMAKE_CURRENT_SOURCE_DIR}/../../Middlewares/ST/netxduo/common/src/nx_ipv6_multicast_join.c    ${CMAKE_CURRENT_SOURCE_DIR}/../../Middlewares/ST/netxduo/common/src/nx_ipv6_multicast_leave.c    ${CMAKE_CURRENT_SOURCE_DIR}/../../Middlewares/ST/netxduo/common/src/nx_ipv6_option_error.c    ${CMAKE_CURRENT_SOURCE_DIR}/../../Middlewares/ST/netxduo/common/src/nx_ipv6_packet_copy.c    ${CMAKE_CURRENT_SOURCE_DIR}/../../Middlewares/ST/netxduo/common/src/nx_ipv6_packet_receive.c    ${CMAKE_CURRENT_SOURCE_DIR}/../../Middlewares/ST/netxduo/common/src/nx_ipv6_packet_send.c    ${CMAKE_CURRENT_SOURCE_DIR}/../../Middlewares/ST/netxduo/common/src/nx_ipv6_prefix_list_add_entry.c    ${CMAKE_CURRENT_SOURCE_DIR}/../../Middlewares/ST/netxduo/common/src/nx_ipv6_prefix_list_delete.c    ${CMAKE_CURRENT_SOURCE_DIR}/../../Middlewares/ST/netxduo/common/src/nx_ipv6_prefix_list_delete_entry.c    ${CMAKE_CURRENT_SOURCE_DIR}/../../Middlewares/ST/netxduo/common/src/nx_ipv6_process_fragment_option.c    ${CMAKE_CURRENT_SOURCE_DIR}/../../Middlewares/ST/netxduo/common/src/nx_ipv6_process_hop_by_hop_option.c    ${CMAKE_CURRENT_SOURCE_DIR}/../../Middlewares/ST/netxduo/common/src/nx_ipv6_process_routing_option.c    ${CMAKE_CURRENT_SOURCE_DIR}/../../Middlewares/ST/netxduo/common/src/nx_ipv6_util.c    ${CMAKE_CURRENT_SOURCE_DIR}/../../Middlewares/ST/netxduo/common/src/nx_link.c    ${CMAKE_CURRENT_SOURCE_DIR}/../../Middlewares/ST/netxduo/common/src/nxd_icmpv6_ra_flag_callback_set.c    ${CMAKE_CURRENT_SOURCE_DIR}/../../Middlewares/ST/netxduo/common/src/nxd_ipv6_address_change_notify.c    ${CMAKE_CURRENT_SOURCE_DIR}/../../Middlewares/ST/netxduo/common/src/nxd_ipv6_address_delete.c    ${CMAKE_CURRENT_SOURCE_DIR}/../../Middlewares/ST/netxduo/common/src/nxd_ipv6_address_get.c    ${CMAKE_CURRENT_SOURCE_DIR}/../../Middlewares/ST/netxduo/common/src/nxd_ipv6_address_set.c    ${CMAKE_CURRENT_SOURCE_DIR}/../../Middlewares/ST/netxduo/common/src/nxd_ipv6_default_router_add.c    ${CMAKE_CURRENT_SOURCE_DIR}/../../Middlewares/ST/netxduo/common/src/nxd_ipv6_default_router_add_internal.c    ${CMAKE_CURRENT_SOURCE_DIR}/../../Middlewares/ST/netxduo/common/src/nxd_ipv6_default_router_delete.c    ${CMAKE_CURRENT_SOURCE_DIR}/../../Middlewares/ST/netxduo/common/src/nxd_ipv6_default_router_entry_get.c    ${CMAKE_CURRENT_SOURCE_DIR}/../../Middlewares/ST/netxduo/common/src/nxd_ipv6_default_router_get.c    ${CMAKE_CURRENT_SOURCE_DIR}/../../Middlewares/ST/netxduo/common/src/nxd_ipv6_default_router_number_of_entries_get.c    ${CMAKE_CURRENT_SOURCE_DIR}/../../Middlewares/ST/netxduo/common/src/nxd_ipv6_default_router_table_init.c    ${CMAKE_CURRENT_SOURCE_DIR}/../../Middlewares/ST/netxduo/common/src/nxd_ipv6_destination_table_find_next_hop.c    ${CMAKE_CURRENT_SOURCE_DIR}/../../Middlewares/ST/netxduo/common/src/nxd_ipv6_disable.c    ${CMAKE_CURRENT_SOURCE_DIR}/../../Middlewares/ST/netxduo/common/src/nxd_ipv6_enable.c    ${CMAKE_CURRENT_SOURCE_DIR}/../../Middlewares/ST/netxduo/common/src/nxd_ipv6_find_default_router_from_address.c    ${CMAKE_CURRENT_SOURCE_DIR}/../../Middlewares/ST/netxduo/common/src/nxd_ipv6_find_max_prefix_length.c    ${CMAKE_CURRENT_SOURCE_DIR}/../../Middlewares/ST/netxduo/common/src/nxd_ipv6_interface_find.c    ${CMAKE_CURRENT_SOURCE_DIR}/../../Middlewares/ST/netxduo/common/src/nxd_ipv6_multicast_interface_join.c    ${CMAKE_CURRENT_SOURCE_DIR}/../../Middlewares/ST/netxduo/common/src/nxd_ipv6_multicast_interface_leave.c    ${CMAKE_CURRENT_SOURCE_DIR}/../../Middlewares/ST/netxduo/common/src/nxd_ipv6_prefix_router_timer_tick.c    ${CMAKE_CURRENT_SOURCE_DIR}/../../Middlewares/ST/netxduo/common/src/nxd_ipv6_raw_packet_send_internal.c    ${CMAKE_CURRENT_SOURCE_DIR}/../../Middlewares/ST/netxduo/common/src/nxd_ipv6_router_lookup.c    ${CMAKE_CURRENT_SOURCE_DIR}/../../Middlewares/ST/netxduo/common/src/nxd_ipv6_router_solicitation_check.c    ${CMAKE_CURRENT_SOURCE_DIR}/../../Middlewares/ST/netxduo/common/src/nxd_ipv6_search_onlink.c    ${CMAKE_CURRENT_SOURCE_DIR}/../../Middlewares/ST/netxduo/common/src/nxd_ipv6_stateless_address_autoconfig_disable.c    ${CMAKE_CURRENT_SOURCE_DIR}/../../Middlewares/ST/netxduo/common/src/nxd_ipv6_stateless_address_autoconfig_enable.c    ${CMAKE_CURRENT_SOURCE_DIR}/../../Middlewares/ST/netxduo/common/src/nxde_icmpv6_ra_flag_callback_set.c    ${CMAKE_CURRENT_SOURCE_DIR}/../../Middlewares/ST/netxduo/common/src/nxde_ipv6_address_change_notify.c    ${CMAKE_CURRENT_SOURCE_DIR}/../../Middlewares/ST/netxduo/common/src/nxde_ipv6_address_delete.c    ${CMAKE_CURRENT_SOURCE_DIR}/../../Middlewares/ST/netxduo/common/src/nxde_ipv6_address_get.c    ${CMAKE_CURRENT_SOURCE_DIR}/../../Middlewares/ST/netxduo/common/src/nxde_ipv6_address_set.c    ${CMAKE_CURRENT_SOURCE_DIR}/../../Middlewares/ST/netxduo/common/src/nxde_ipv6_default_router_add.c    ${CMAKE_CURRENT_SOURCE_DIR}/../../Middlewares/ST/netxduo/common/src/nxde_ipv6_default_router_delete.c    ${CMAKE_CURRENT_SOURCE_DIR}/../../Middlewares/ST/netxduo/common/src/nxde_ipv6_default_router_entry_get.c    ${CMAKE_CURRENT_SOURCE_DIR}/../../Middlewares/ST/netxduo/common/src/nxde_ipv6_default_router_get.c    ${CMAKE_CURRENT_SOURCE_DIR}/../../Middlewares/ST/netxduo/common/src/nxde_ipv6_default_router_number_of_entries_get.c    ${CMAKE_CURRENT_SOURCE_DIR}/../../Middlewares/ST/netxduo/common/src/nxde_ipv6_disable.c    ${CMAKE_CURRENT_SOURCE_DIR}/../../Middlewares/ST/netxduo/common/src/nxde_ipv6_enable.c    ${CMAKE_CURRENT_SOURCE_DIR}/../../Middlewares/ST/netxduo/common/src/nxde_ipv6_multicast_interface_join.c    ${CMAKE_CURRENT_SOURCE_DIR}/../../Middlewares/ST/netxduo/common/src/nxde_ipv6_multicast_interface_leave.c    ${CMAKE_CURRENT_SOURCE_DIR}/../../Middlewares/ST/netxduo/common/src/nxde_ipv6_stateless_address_autoconfig_disable.c    ${CMAKE_CURRENT_SOURCE_DIR}/../../Middlewares/ST/netxduo/common/src/nxde_ipv6_stateless_address_autoconfig_enable.c    ${CMAKE_CURRENT_SOURCE_DIR}/../../Middlewares/ST/netxduo/common/src/nxd_nd_cache_entry_delete.c    ${CMAKE_CURRENT_SOURCE_DIR}/../../Middlewares/ST/netxduo/common/src/nxd_nd_cache_entry_set.c    ${CMAKE_CURRENT_SOURCE_DIR}/../../Middlewares/ST/netxduo/common/src/nxd_nd_cache_hardware_address_find.c    ${CMAKE_CURRENT_SOURCE_DIR}/../../Middlewares/ST/netxduo/common/src/nxd_nd_cache_invalidate.c    ${CMAKE_CURRENT_SOURCE_DIR}/../../Middlewares/ST/netxduo/common/src/nxd_nd_cache_ip_address_find.c    ${CMAKE_CURRENT_SOURCE_DIR}/../../Middlewares/ST/netxduo/common/src/nx_http_proxy_client.c    ${CMAKE_CURRENT_SOURCE_DIR}/../../Middlewares/ST/netxduo/common/drivers/ethernet/lan8742/nx_stm32_phy_driver.c)# Link directories setupset(MX_LINK_DIRS)# Project static librariesset(MX_LINK_LIBS     STM32_Drivers    ${TOOLCHAIN_LINK_LIBRARIES}    ThreadX	NetXDuo	)# Interface library for includes and symbolsadd_library(stm32cubemx INTERFACE)target_include_directories(stm32cubemx INTERFACE ${MX_Include_Dirs})target_compile_definitions(stm32cubemx INTERFACE ${MX_Defines_Syms})# Create STM32_Drivers static libraryadd_library(STM32_Drivers OBJECT)target_sources(STM32_Drivers PRIVATE ${STM32_Drivers_Src})target_link_libraries(STM32_Drivers PUBLIC stm32cubemx)# Create ThreadX static libraryadd_library(ThreadX OBJECT)target_sources(ThreadX PRIVATE ${ThreadX_Src})target_link_libraries(ThreadX PUBLIC stm32cubemx)# Create NetXDuo static libraryadd_library(NetXDuo OBJECT)target_sources(NetXDuo PRIVATE ${NetXDuo_Src})target_link_libraries(NetXDuo PUBLIC stm32cubemx)# Add STM32CubeMX generated application sources to the projecttarget_sources(${CMAKE_PROJECT_NAME} PRIVATE ${MX_Application_Src})# Link directories setuptarget_link_directories(${CMAKE_PROJECT_NAME} PRIVATE ${MX_LINK_DIRS})# Add libraries to the projecttarget_link_libraries(${CMAKE_PROJECT_NAME} ${MX_LINK_LIBS})# Add the map file to the list of files to be removed with 'clean' targetset_target_properties(${CMAKE_PROJECT_NAME} PROPERTIES ADDITIONAL_CLEAN_FILES ${CMAKE_PROJECT_NAME}.map)# Validate that STM32CubeMX code is compatible with C standardif((CMAKE_C_STANDARD EQUAL 90) OR (CMAKE_C_STANDARD EQUAL 99))    message(ERROR "Generated code requires C11 or higher")endif()

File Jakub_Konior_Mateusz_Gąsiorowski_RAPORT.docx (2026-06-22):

| AKADEMIA GÓRNICZO-HUTNICZA

Raport z projektu

Thermocouple Temperature Logger

z przedmiotu

Sensory w Aplikacjach Wbudowanych

Elektronika i Telekomunikacja - Systemy Wbudowane, rok I studiów magisterskich

Jakub Konior

Mateusz Gąsiorowski

22.06.2026r

Spis treści

# 1. Opis i założenia projektu

## 1.1. Założenia projektowe i wysokopoziomowy opis projektu

### 1.1.1. Założenia projektowe odnośnie warstwy sprzętowej

- Mikrokontroler: Rodzina STM32H5 (ARM Cortex-M33)
- Układ pomiarowy: Analog Devices LTC2983 (Multi-Sensor High Accuracy Digital Temperature Measurement System)
- Wyświetlacz: Monochromatyczny LCD / OLED 2004
- Interfejsy:
  - Gniazdo Ethernet (RJ45)
  - Slot na kartę pamięci uSD
- Złącza dla 8-10 termopar.
- Sterowanie lokalne:
  - Enkoder obrotowy z przyciskiem
  - przyciski funkcyjne pod ekranem.
- Zasilanie: Zasilacz 230VAC → 5VDC-12VDC w postaci gotowego modułu na PCB.

### 1.1.2. Założenia projektowe odnośnie oprogramowania,

- System operacyjny (RTOS): Eclipse ThreadX
- Protokół komunikacyjny: SCPI (Standard Commands for Programmable Instruments).
- System plików: Obsługa FAT/exFAT dla karty SD.

### 1.1.3. Opis projektu:

- Precyzyjny pomiar: Odczyt temperatur z 8-10 niezależnych termopar przy użyciu specjalizowanego układu LTC2983.
- Logowanie danych: Zapis historii pomiarów bezpośrednio na kartę pamięci MicroSD.
- Komunikacja z PC: Zdalny odczyt i sterowanie przez interfejs Ethernet z wykorzystaniem protokołu VISA / SCPI.
- Podgląd na żywo: Wyświetlanie aktualnych temperatur oraz stanu urządzenia na monochromatycznym ekranie LCD/OLED.
- Interfejs użytkownika (HMI): Wygodne sterowanie za pomocą enkodera obrotowego oraz dedykowanych przycisków umieszczonych pod wyświetlaczem.

## 1.2. Podział odpowiedzialności

Tabelka z przypisaniem poszczególnych kamieni milowych/funkcjonalności do członków projektu

Osoba | Podział odpowiedzialności
Mateusz Gąsiorowski | Dobór komponentów, utworzenie schematu płytek
Jakub Konior | Konfiguracja peryferiów, oprogramowanie podstawowych funkcji
Mateusz Gąsiorowski | Layout PCB, projekt PCB kompatybilny obudowy
Jakub Konior | Oprogramowanie i testy komunikacji VISA-SCPI
Mateusz Gąsiorowski | Montaż i uruchomienie PCB

# 2. Sprzęt

## 2.1. Wybór komponentów

- STM32H563ZI - zbliżony mikrokontroler do wykorzystanego na Nucleo-144, 2MB pamięci Flash dają zapas miejsca na obsługę wyświetlacza oraz komunikacji Ethernet VISA.
- LTC2983 - układ od Analog Devices pozwalający z multiplexerem 20 kanałowym i kilkukanałowym precyzyjnym ADC, pozwala na elastyczną konfigurację podłączonych czujników (w założeniu projektu termopar). W układzie zintegrowano kompleksowo pakiet “układów” wymagany do precyzyjnych pomiarów → referencyjne źródła napiecia, multipleksery, przetworniki ADC, komunikację po SPI.
- LAN8742A - dokładnie ten sam układ PHY co na Nucleo-144, pozwoli na pisanie i testowanie oprogramowania w trakcie projektowania i wykonywania PCB.
- Wyświetlacz OLED/LCD 2004 alfanumeryczny – wybrano z uwagi na łatwość wykorzystania i oprogramowania. Pozwoli na wyświetlenie 8-10 równoległych 3-4 cyfrowych odczytów na raz, w przypadku wymaganej większej dokładności odczytu możliwe jest osiągnięcie tego przez podział odczytów na 2 (lub więcej) stron.
- Temopary typu K - budżetowe, ale wystarczające rozwiązanie do większości wykonywanych w labolatoriach elektronicznych pomiarów.

## 2.2. Opis schematu

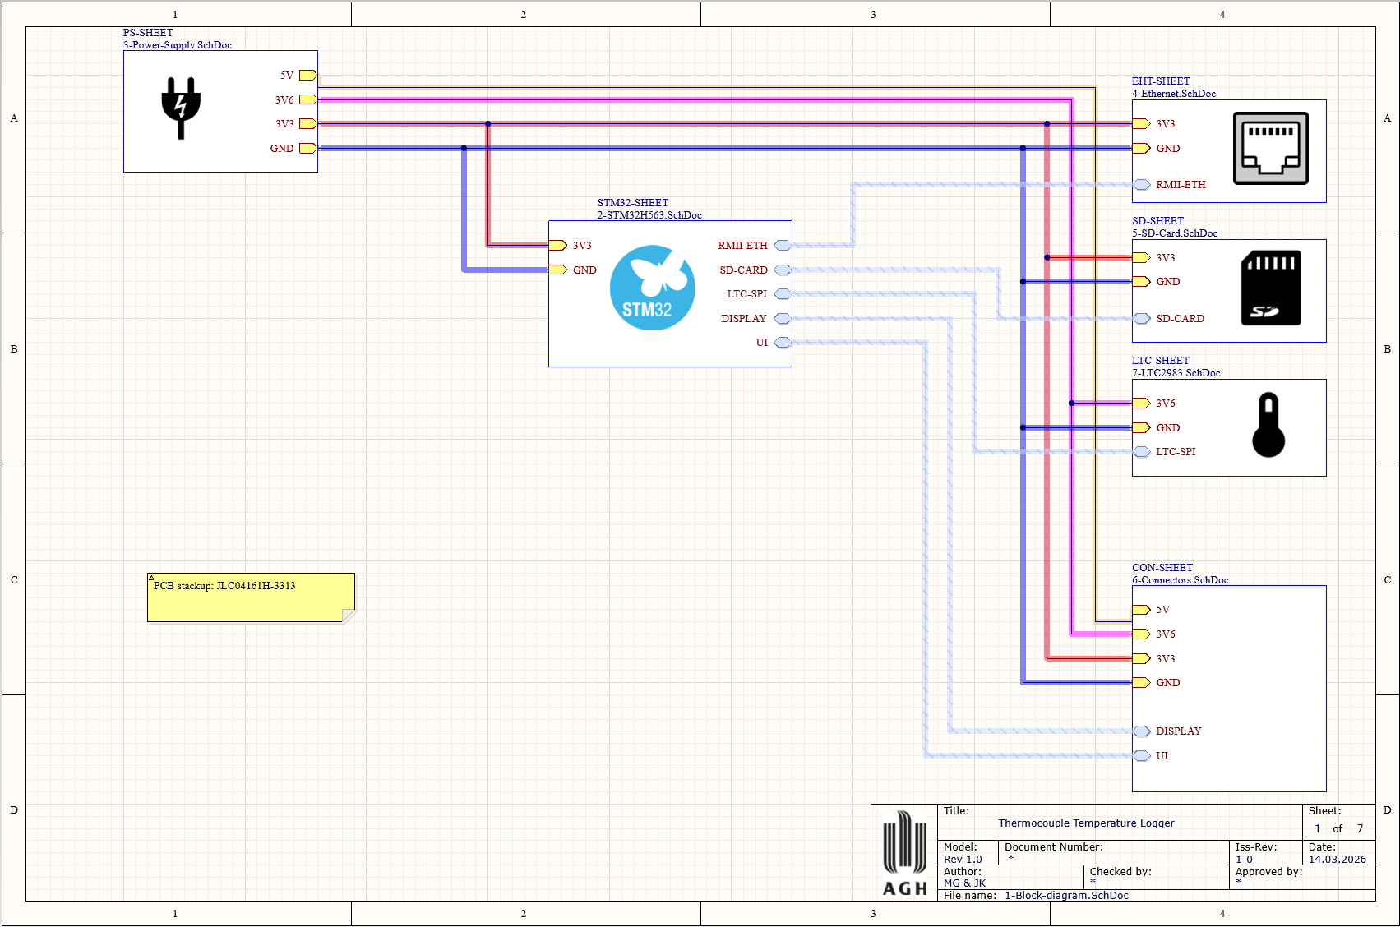
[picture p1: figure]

Rysunek 2.2.1 - Schemat ideowy 1-Block-diagram

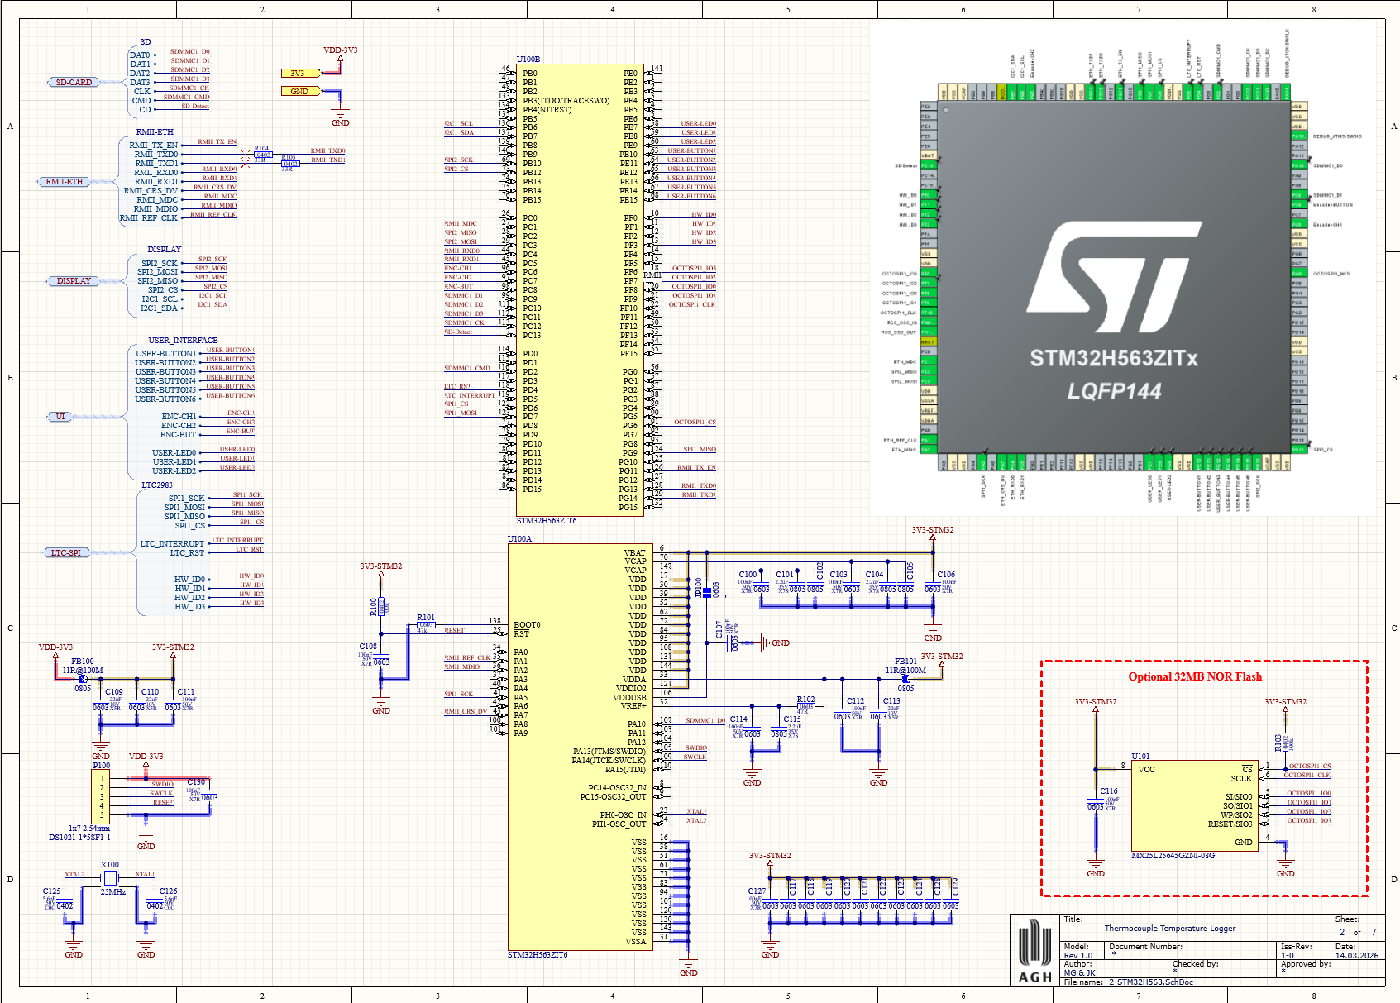
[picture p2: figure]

Rysunek 2.2.2 - Schemat ideowy 2-MCU

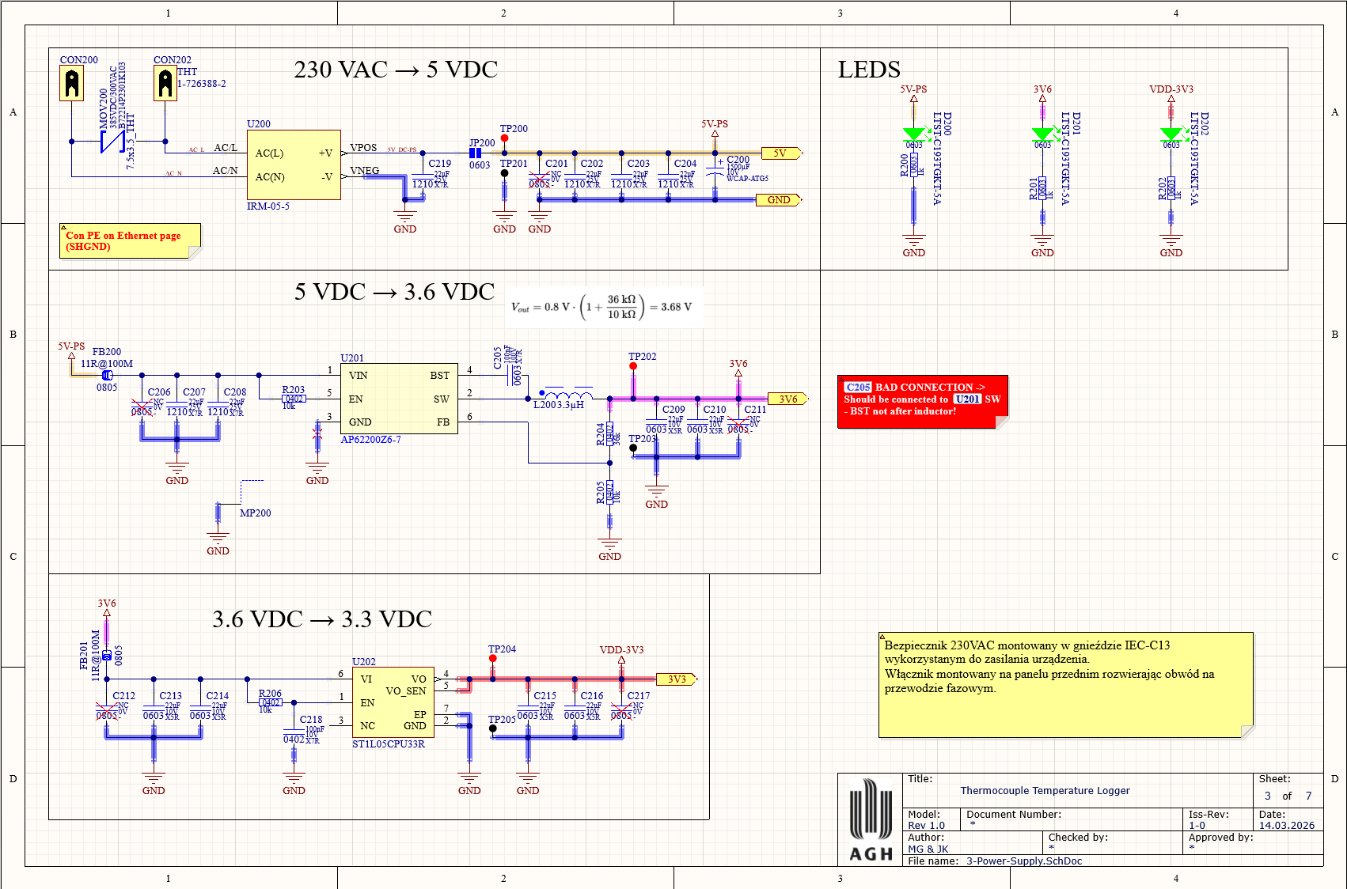
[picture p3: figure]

Rysunek 2.2.3 - Schemat ideowy 3-Power-Supply

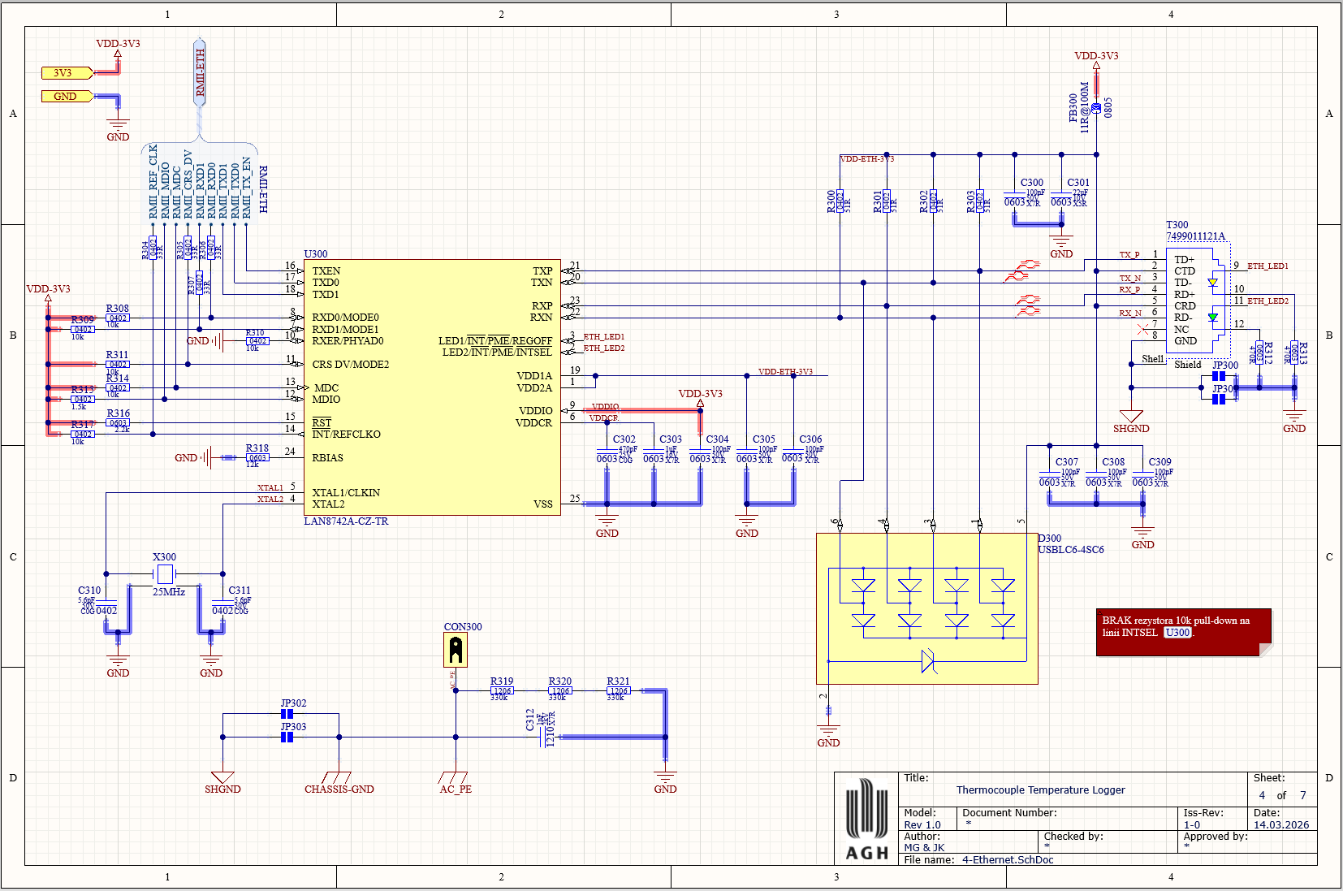
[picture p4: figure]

Rysunek 2.2.4 - Schemat ideowy 4-Ethernet

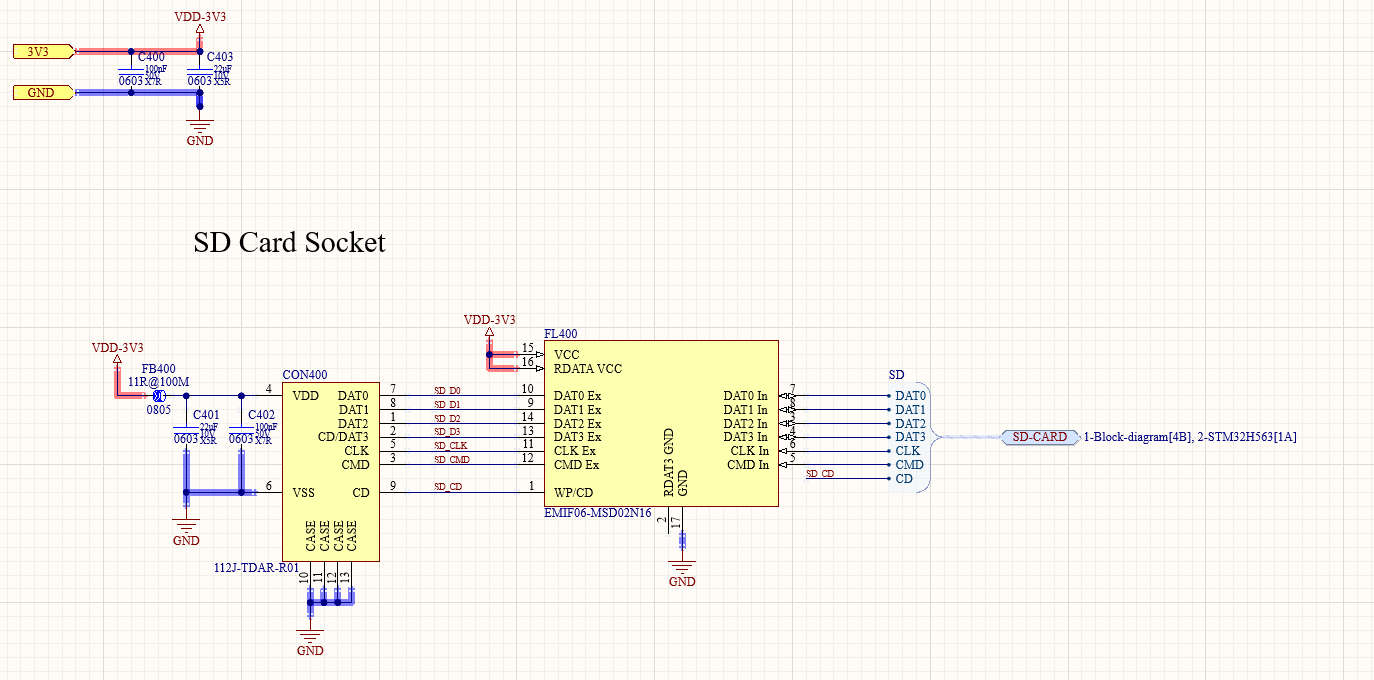
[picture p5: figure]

Rysunek 2.2.5 - Schemat ideowy 5-SD-Card

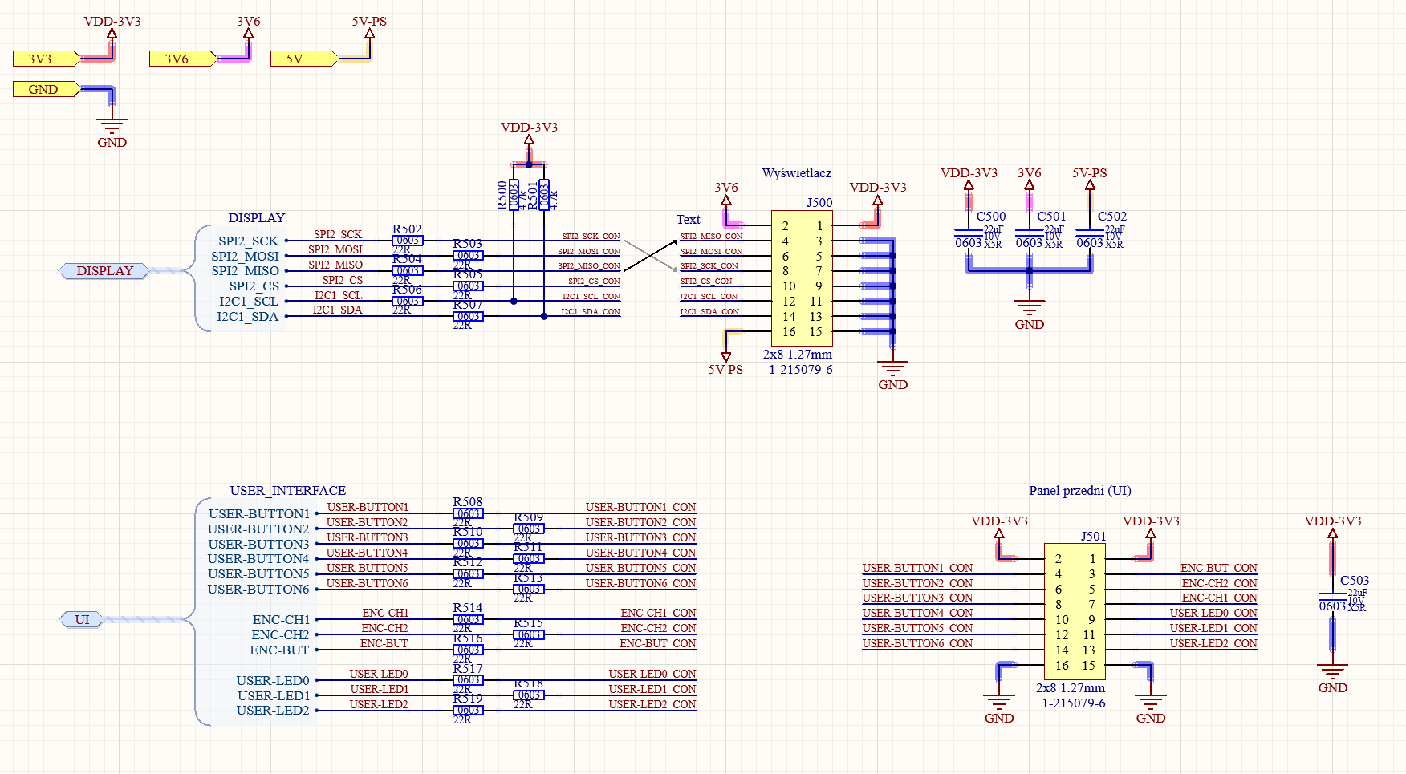
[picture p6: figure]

Rysunek 2.2.6 - Schemat ideowy 6-Connectors

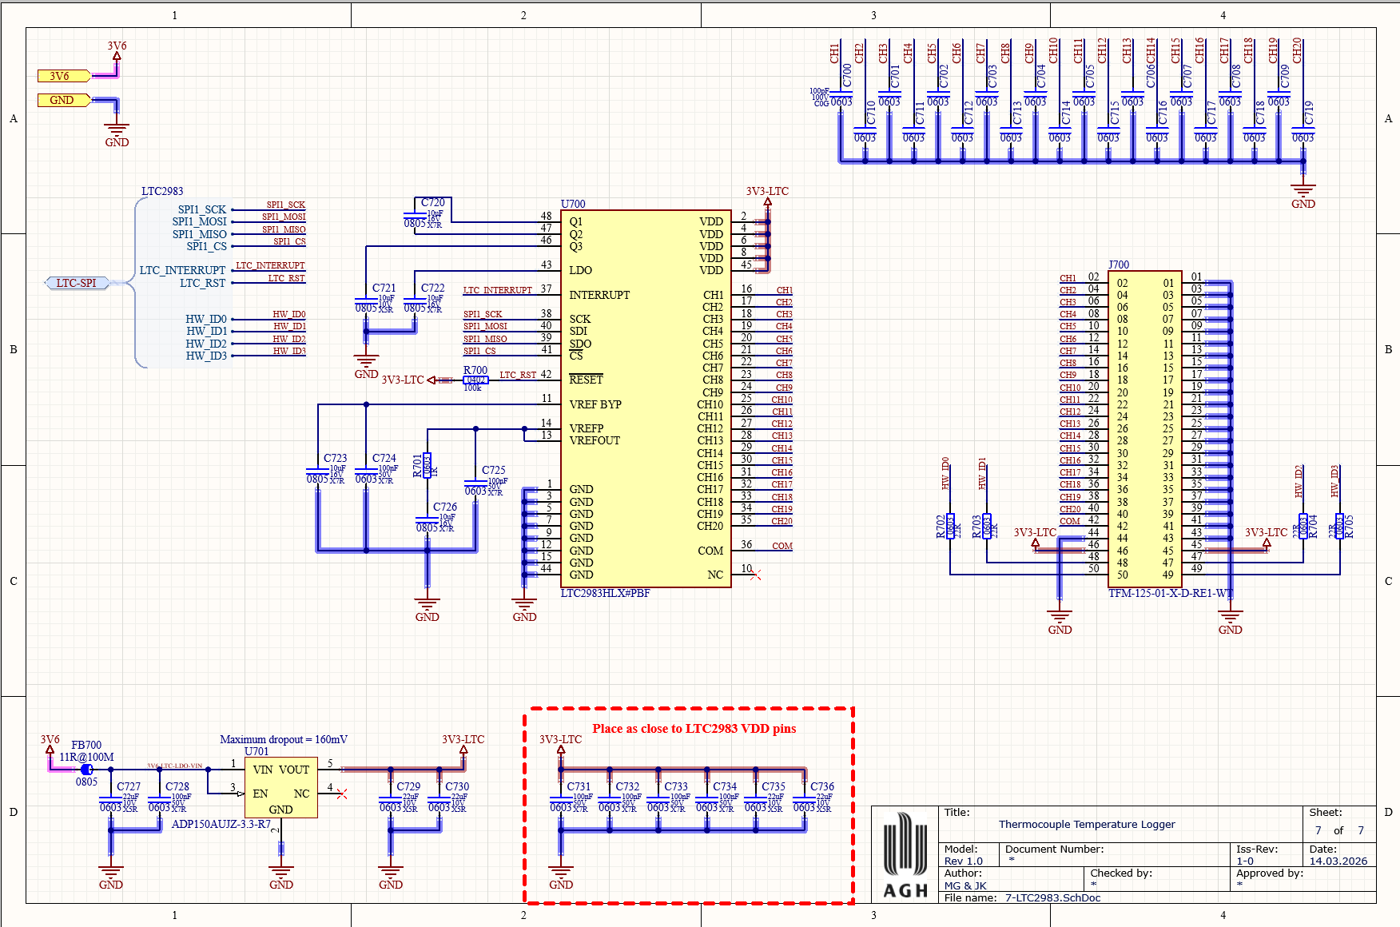
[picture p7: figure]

Rysunek 2.2.7 - Schemat ideowy 7-LTC2983

## 2.3. PCB

### 2.3.1 Projekt PCB

Obrys płytki zaprojektowano tak aby boczne krawędzie (prawa i lewa strona) wsuwały się w prowadnice aluminiowej obudowy. PCB rozdzielono na kilka sekcji:

- Zasilanie 230VAC – u samej góry płytki aby zapewnić jak największą separację między sekcją analogową (LTC2983) a wysokim napięciem.
- Zasilania DC – w środkowej części PCB, przetwornica 5V → 3.6V i poniżej LDO od MCU na 3.3V.
- STM32H563ZI – w centralnej części PCB – w celu zapewniania optymalnego routingu RMII jak i SPI / UART.
- Ethernet – bezpośrednio przy złączu umieszczonym z tyłu PCB (na tylnym panelu urządzenia).
- LTC2983 i złącze do panelu czujników – w prawym dolnym rogu – największa separacja od pozostałych sygnałów high-speed i wysoko napięciowych. Przy układzie zastosowano osobny LDO ultra-low-noise w celu ograniczenia przenikania zakłóceń z innych układów.
- Karta mikroSD – z uwagi na konieczność umieszczenia karty na przednim panelu (wygoda korzystania z urządzenia) umieszczono bliżej lewej krawędzi.
- Lewa strona PCB „cable-tie” – miejsce do zabezpieczenia przewodów 230V idących do włącznika urządzenia na frontowym panelu.
- Konektory micro-match – równolegle do dolnej krawędzi – aby wygodnie poprowadzić taśmy do przedniego panelu (wyświetlacz i interfejs użytkownika).

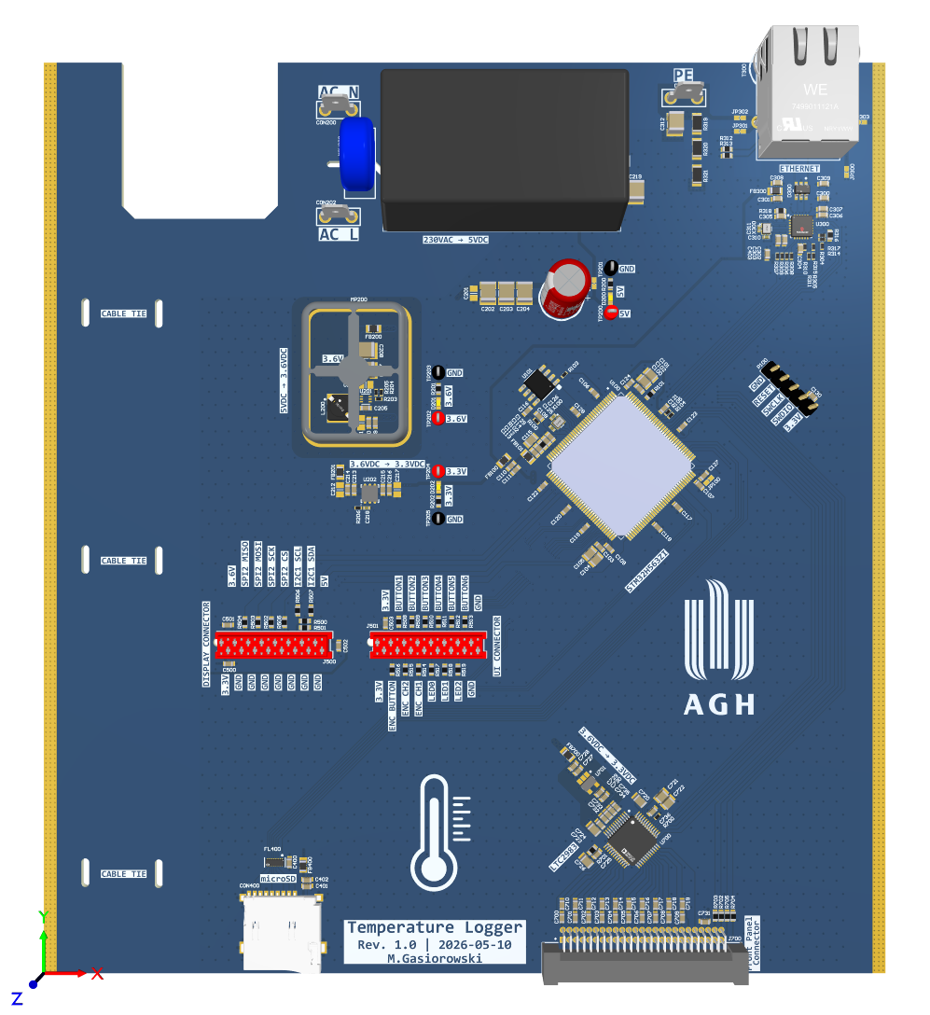
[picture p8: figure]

Rysunek 2.3.1 – widok górny PCB

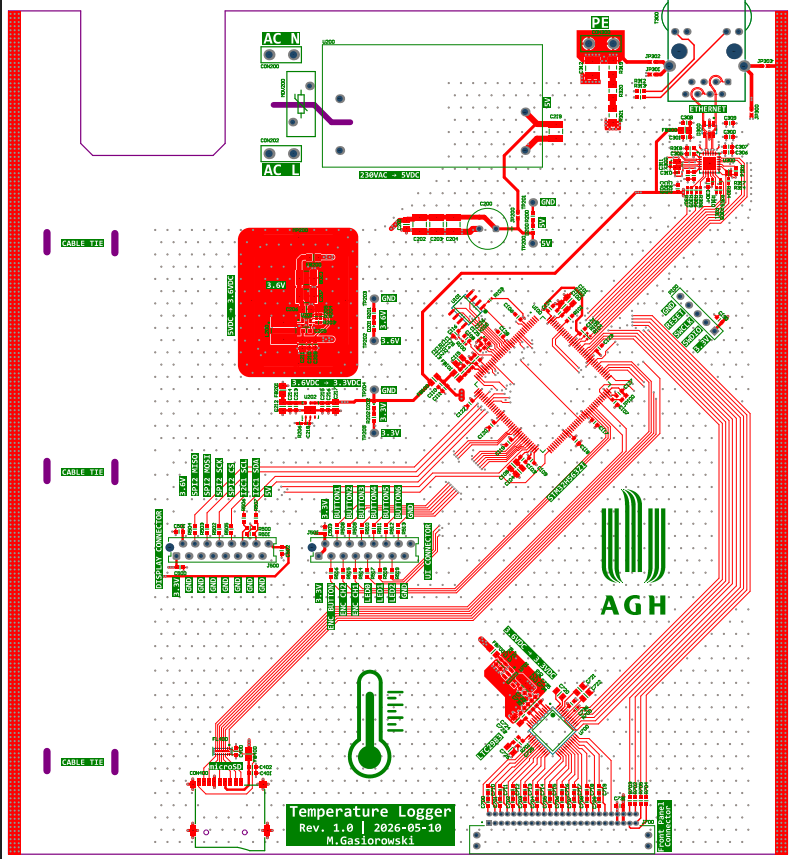
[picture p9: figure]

Rysunek 2.3.2 –widok warstwy top

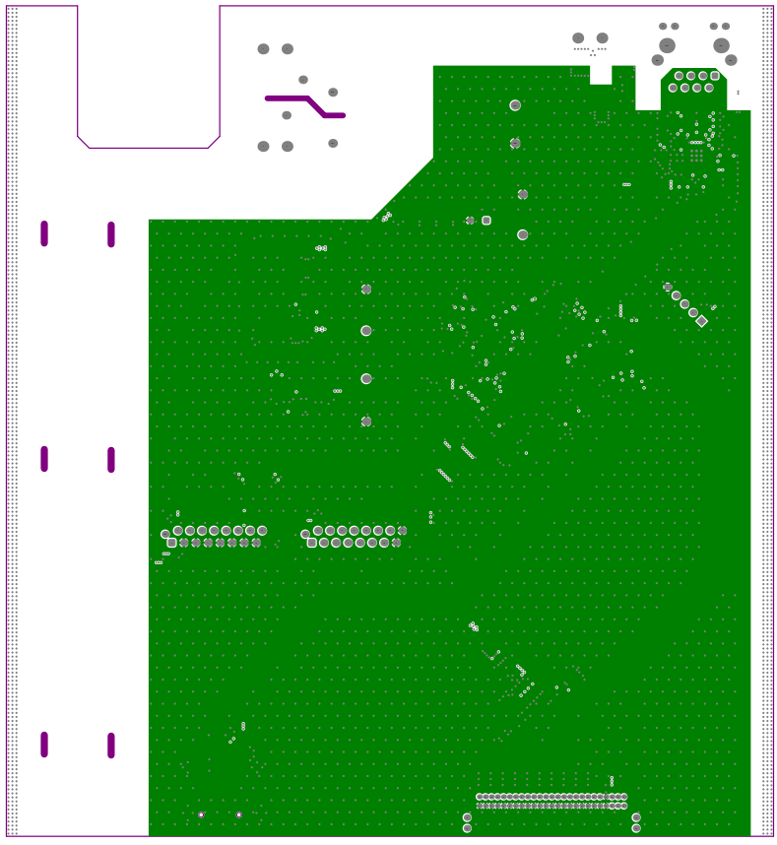
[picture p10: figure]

Rysunek 2.3.3 –widok warstwy inner1

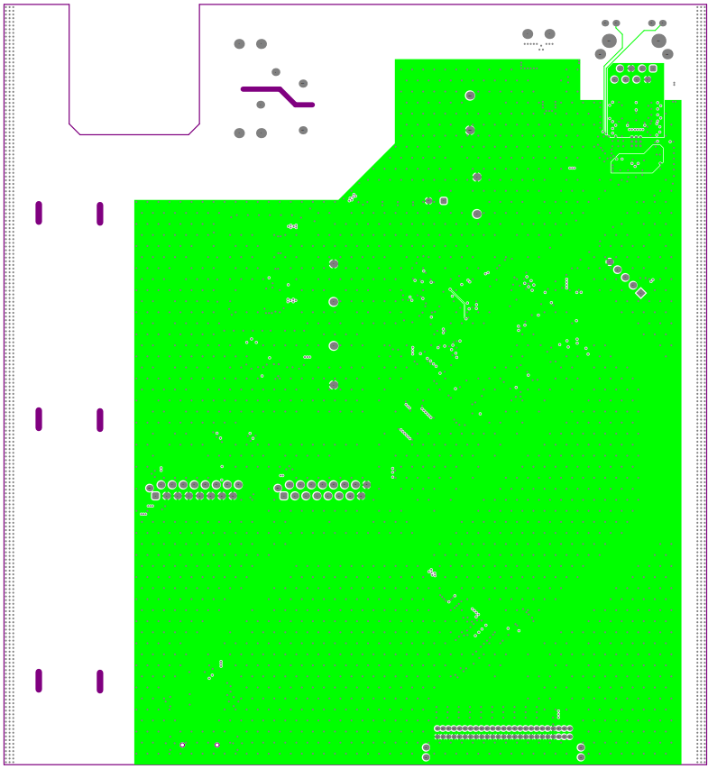
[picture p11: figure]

Rysunek 2.33 –widok warstwy inner2

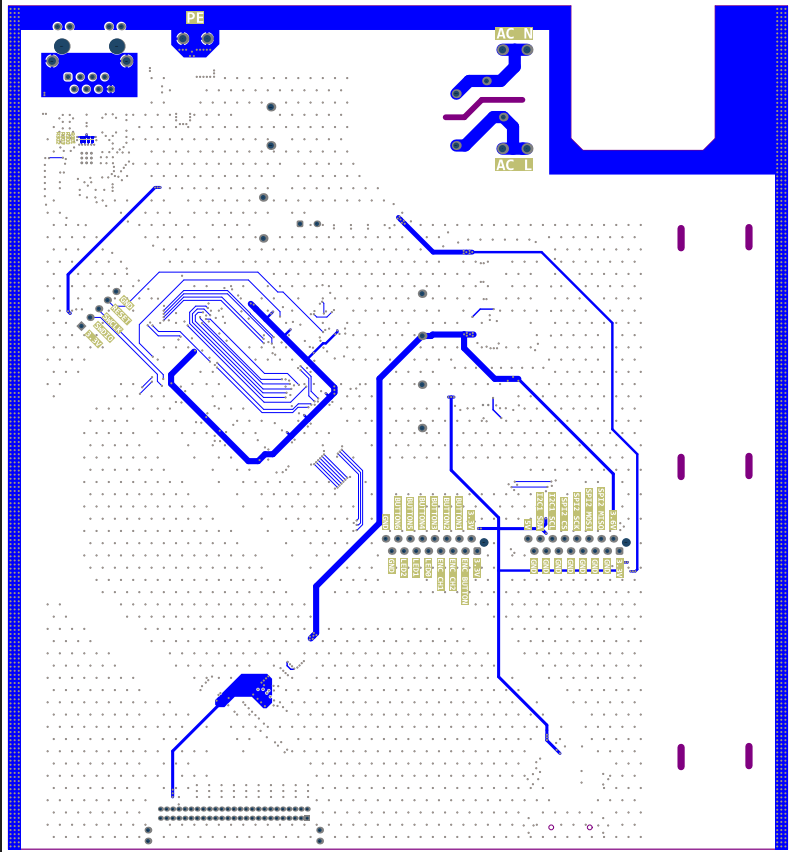
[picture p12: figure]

Rysunek 2.3.4 –widok warstwy bottom

### 2.3.2 montaż i uruchomienie

Z uwagi na koszt elementów na PCB przyjęto iteracyjny sposób montażu i uruchamiania kolejnych sekcji – po montażu wszystkich elementów pasywnych montowano i uruchamiano kolejno:

- Zasilanie (bez zasilacza 230V) – przy uruchomieniu zaobserwowano brak rozruchu przetwornicy 5V → 3.6V. Po sprawdzeniu poprawności montażu wykryto błąd w PCB – brak wylewki GND w przetwornicy.

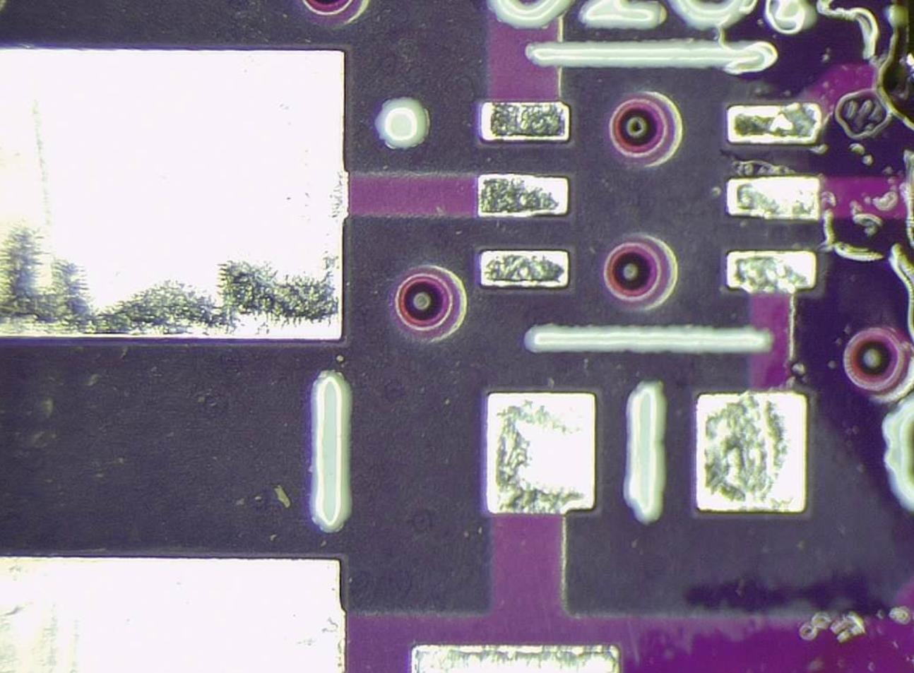
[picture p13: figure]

Rysunek 2.3.5 – widok PCB przy przetwornicy 3.6V.

Po wykonaniu połączeń przewodem typu kynar lub mostkiem ze spoiwa, wykonano kolejną próbę uruchomienia. Zmierzono napięcie na pinie wyjściowym przetwornicy 2.3V zamiast 3.7V, przy pomocy oscyloskopu zmierzono przebieg na pinie SW – częstotliwość pracy była za niska. Znaleziono problem z błędnym połączeniem kondensatora BST.

Wykonano poprawę PCB poprzez przecięcie ścieżki i wykonania połączenia przewodem typu kynar.

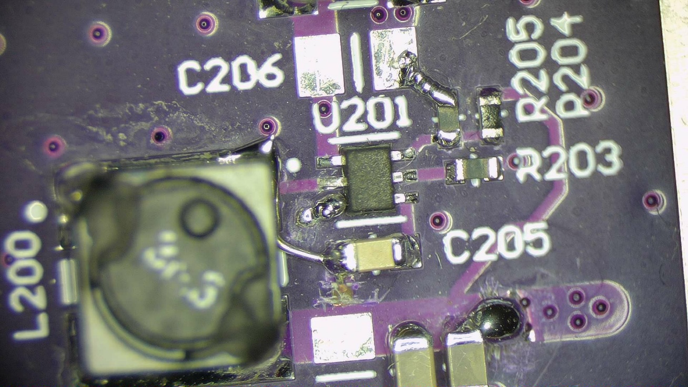
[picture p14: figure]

Rysunek 2.3.5 – widok poprawioną PCB przy przetwornicy 3.6V.

- Stabilizator na 3.3V od mikrokontrolera działał poprawnie (zmierzone napięcie na wyjściu 3.3V)
- Zamontowano mikroprocesor STM32H563ZI i sprawdzono komunikację z mikrokontrolerem za pomocą ST-LINK-V2. Po wgraniu kodu testowego typu blink sprawdzono na wyjściu czy program działa poprawnie.
- Zamontowano układ LAN8742A – wgrano program testowy w celu sprawdzenia komunikacji – program nie działał poprawnie, podczas debugowania zmierzono, że na zegarze RMII nie jest generowany sygnał CLK. Po weryfikacji schematu i analizie noty katalogowej znaleziono błąd – brakujący rezystor pull-down na pinie INTSEL

(który funkcję dzieli z diodą LED na złączu RJ45).

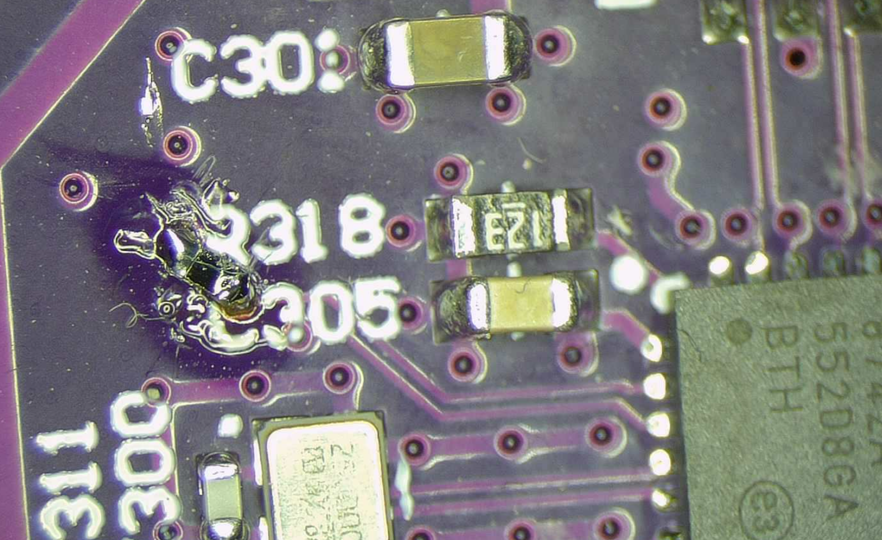
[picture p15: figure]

Rysunek 2.3.5 – widok poprawioną PCB przy układzie LAN8742A.

- Sprawdzono działanie DHCP i ICMP – został przydzielony adres IP oraz odpowiada na ping.
- Zamontowano pozostałe komponenty poza zasilaczem 230V oraz układem LTC2983.
- Układ wymaga dalszych testów uruchomieniowych.

## 2.4. Mechanika

Wykorzystana zostanie obudowa Kradex ZR185.180.65 - wykonana z aluminium będzie odporna na uszkodzenia w warunkach labolatoryjnych, dodatkowo zapewniając ekranowanie urządzenia.

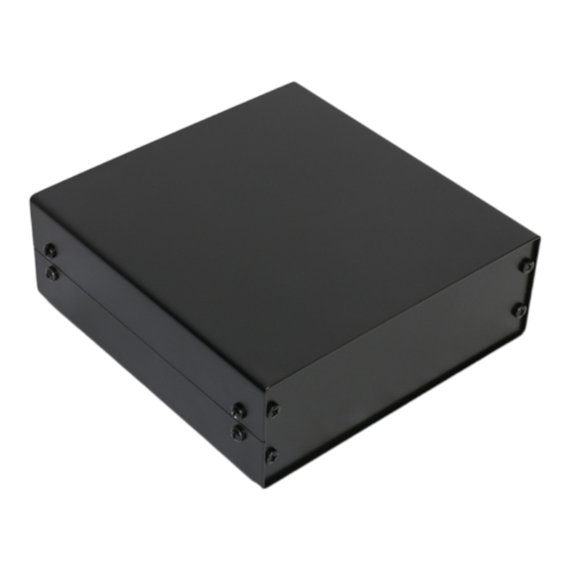
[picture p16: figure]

Rysunek 2.4.1 - Widok obudowy ZR185.180.65 [Kradex.com.pl]

# 3. Oprogramowanie

  3.1 Architektura oprogramowania

Oprogramowanie urządzenia zostało napisane w języku C++17 z wykorzystaniem środowiska STM32CubeMX, kompilatora GCC ARM Embedded oraz systemu budowania CMake. Za zarządzanie zadaniami czasu rzeczywistego odpowiada system operacyjny Azure RTOS ThreadX, natomiast komunikacja sieciowa realizowana jest przez stos TCP/IP Azure RTOS NetXDuo.

Podczas uruchamiania urządzenia wykonywana jest standardowa procedura inicjalizacji mikrokontrolera obejmująca konfigurację zegarów systemowych, inicjalizację peryferiów oraz uruchomienie interfejsu diagnostycznego UART. Następnie sterowanie przekazywane jest do jądra ThreadX, które rozpoczyna pracę harmonogramu i uruchamia wszystkie zadania aplikacyjne.

Zastosowanie systemu czasu rzeczywistego umożliwia rozdzielenie funkcjonalności urządzenia na niezależne wątki wykonujące swoje zadania równolegle. Takie podejście zwiększa przejrzystość kodu oraz ułatwia dalszą rozbudowę projektu.

3.2 Organizacja wątków ThreadX

W systemie zaimplementowano cztery podstawowe wątki aplikacyjne.

LedThread

Wątek odpowiedzialny za sygnalizację działania systemu. Jego zadaniem jest okresowe przełączanie diod LED oraz generowanie komunikatów diagnostycznych przesyłanych przez interfejs UART. Wątek ten pełni również funkcję kontrolną pozwalającą zweryfikować poprawność działania harmonogramu ThreadX.

LCDThread

Wątek odpowiedzialny za aktualizację informacji prezentowanych na wyświetlaczu LCD. Dane pomiarowe pobierane są z modułu ChannelManager i cyklicznie wyświetlane użytkownikowi. W przyszłości planowane jest rozszerzenie funkcjonalności o obsługę menu konfiguracyjnego.

EncoderThread

Wątek realizuje obsługę enkodera inkrementalnego wykorzystywanego jako podstawowy element sterowania urządzeniem. Pozycja enkodera odczytywana jest przy pomocy timera TIM3 pracującego w trybie sprzętowego dekodera kwadraturowego.

Wątek monitoruje zarówno kierunek obrotu, jak i stan przycisku zintegrowanego z enkoderem. Pozwala to na wygodną zmianę parametrów konfiguracyjnych bez konieczności stosowania wielu przycisków.

EthThread

Wątek odpowiedzialny za obsługę komunikacji sieciowej. Po uruchomieniu inicjalizowany jest stos TCP/IP NetXDuo, konfiguracja interfejsu Ethernet oraz serwer TCP nasłuchujący na porcie 5025.

Wątek odbiera polecenia SCPI przesyłane przez klienta sieciowego, przekazuje je do parsera komend oraz odsyła odpowiedzi do użytkownika.

  3.2 Moduł ChannelManager

Centralnym elementem logiki aplikacji jest moduł ChannelManager zarządzający wszystkimi kanałami pomiarowymi.

Każdy z ośmiu kanałów posiada własną konfigurację obejmującą:

- typ termopary,
- wartość offsetu kalibracyjnego,
- współczynnik wzmocnienia,
- aktualną temperaturę,
- status błędów.

Moduł udostępnia jednolity interfejs dla pozostałych części programu, dzięki czemu wyświetlacze, parser SCPI oraz przyszły sterownik układu LTC korzystają z tych samych danych.

Dodatkowo ChannelManager obsługuje mechanizm pamięci konfiguracji umożliwiający zapis parametrów w dziesięciu niezależnych slotach użytkownika.

Na obecnym etapie projektu moduł generuje symulowane dane pomiarowe wykorzystywane do testowania pozostałych elementów systemu.

  3.3 Komunikacja SCPI

W celu zapewnienia kompatybilności z urządzeniami laboratoryjnymi wykorzystano standard SCPI (Standard Commands for Programmable Instruments).

Obsługa komend realizowana jest przez moduł ScpiParser. Parser umożliwia analizę pojedynczych poleceń, komend złożonych rozdzielonych średnikami oraz zapytań zakończonych znakiem zapytania.

Aktualnie zaimplementowano między innymi następujące polecenia:

- *IDN? – identyfikacja urządzenia,
- *RST – przywrócenie ustawień domyślnych,
- CONF:TC:TYPE – konfiguracja typu termopary,
- MEAS:TEMP – odczyt temperatury wybranego kanału,
- READ? – odczyt wszystkich kanałów,
- CAL:OFFSET – ustawienie korekcji offsetu,
- STAT:CHAN? – odczyt stanu kanału,
- MEM:STORE – zapis konfiguracji do pamięci.

Dzięki zastosowaniu standardu SCPI urządzenie może być sterowane z poziomu aplikacji laboratoryjnych bez konieczności opracowywania własnego protokołu komunikacyjnego.

  3.4 Obsługa karty SD

Moduł SdCard odpowiada za komunikację z kartą pamięci SD wykorzystując kontroler SDMMC1 mikrokontrolera.

Sterownik realizuje:

- inicjalizację karty,
- odczyt sektorów,
- zapis sektorów,
- wykrywanie obecności nośnika,
- odczyt parametrów karty.

Ze względu na wielowątkowy charakter aplikacji dostęp do karty zabezpieczony został przy pomocy mutexa ThreadX. Rozwiązanie to eliminuje ryzyko jednoczesnego dostępu kilku zadań do tego samego urządzenia i zwiększa niezawodność działania systemu.

Maksymalny czas oczekiwania na zakończenie operacji odczytu lub zapisu wynosi 5 sekund.

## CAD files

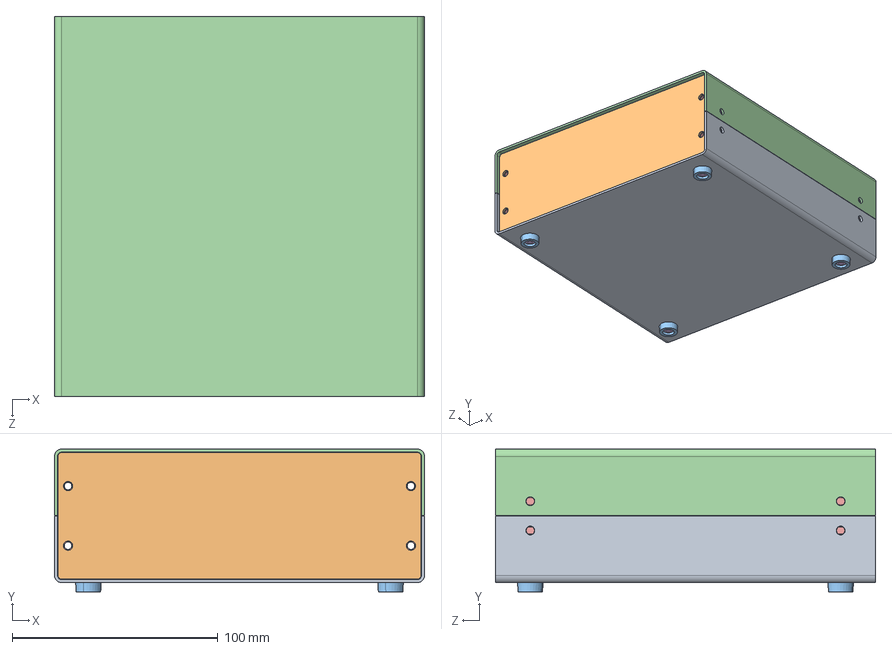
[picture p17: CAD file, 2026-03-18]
HARDWARE/Enclosure/ZR185_180_65_step.step
180.0 x 69.5 x 185.0 mm
Base(Domy挈na)
Front x 2
small_foot x 4
Cover
Rail_v1 x 2
Klin x 4
Blokada_v2 x 8

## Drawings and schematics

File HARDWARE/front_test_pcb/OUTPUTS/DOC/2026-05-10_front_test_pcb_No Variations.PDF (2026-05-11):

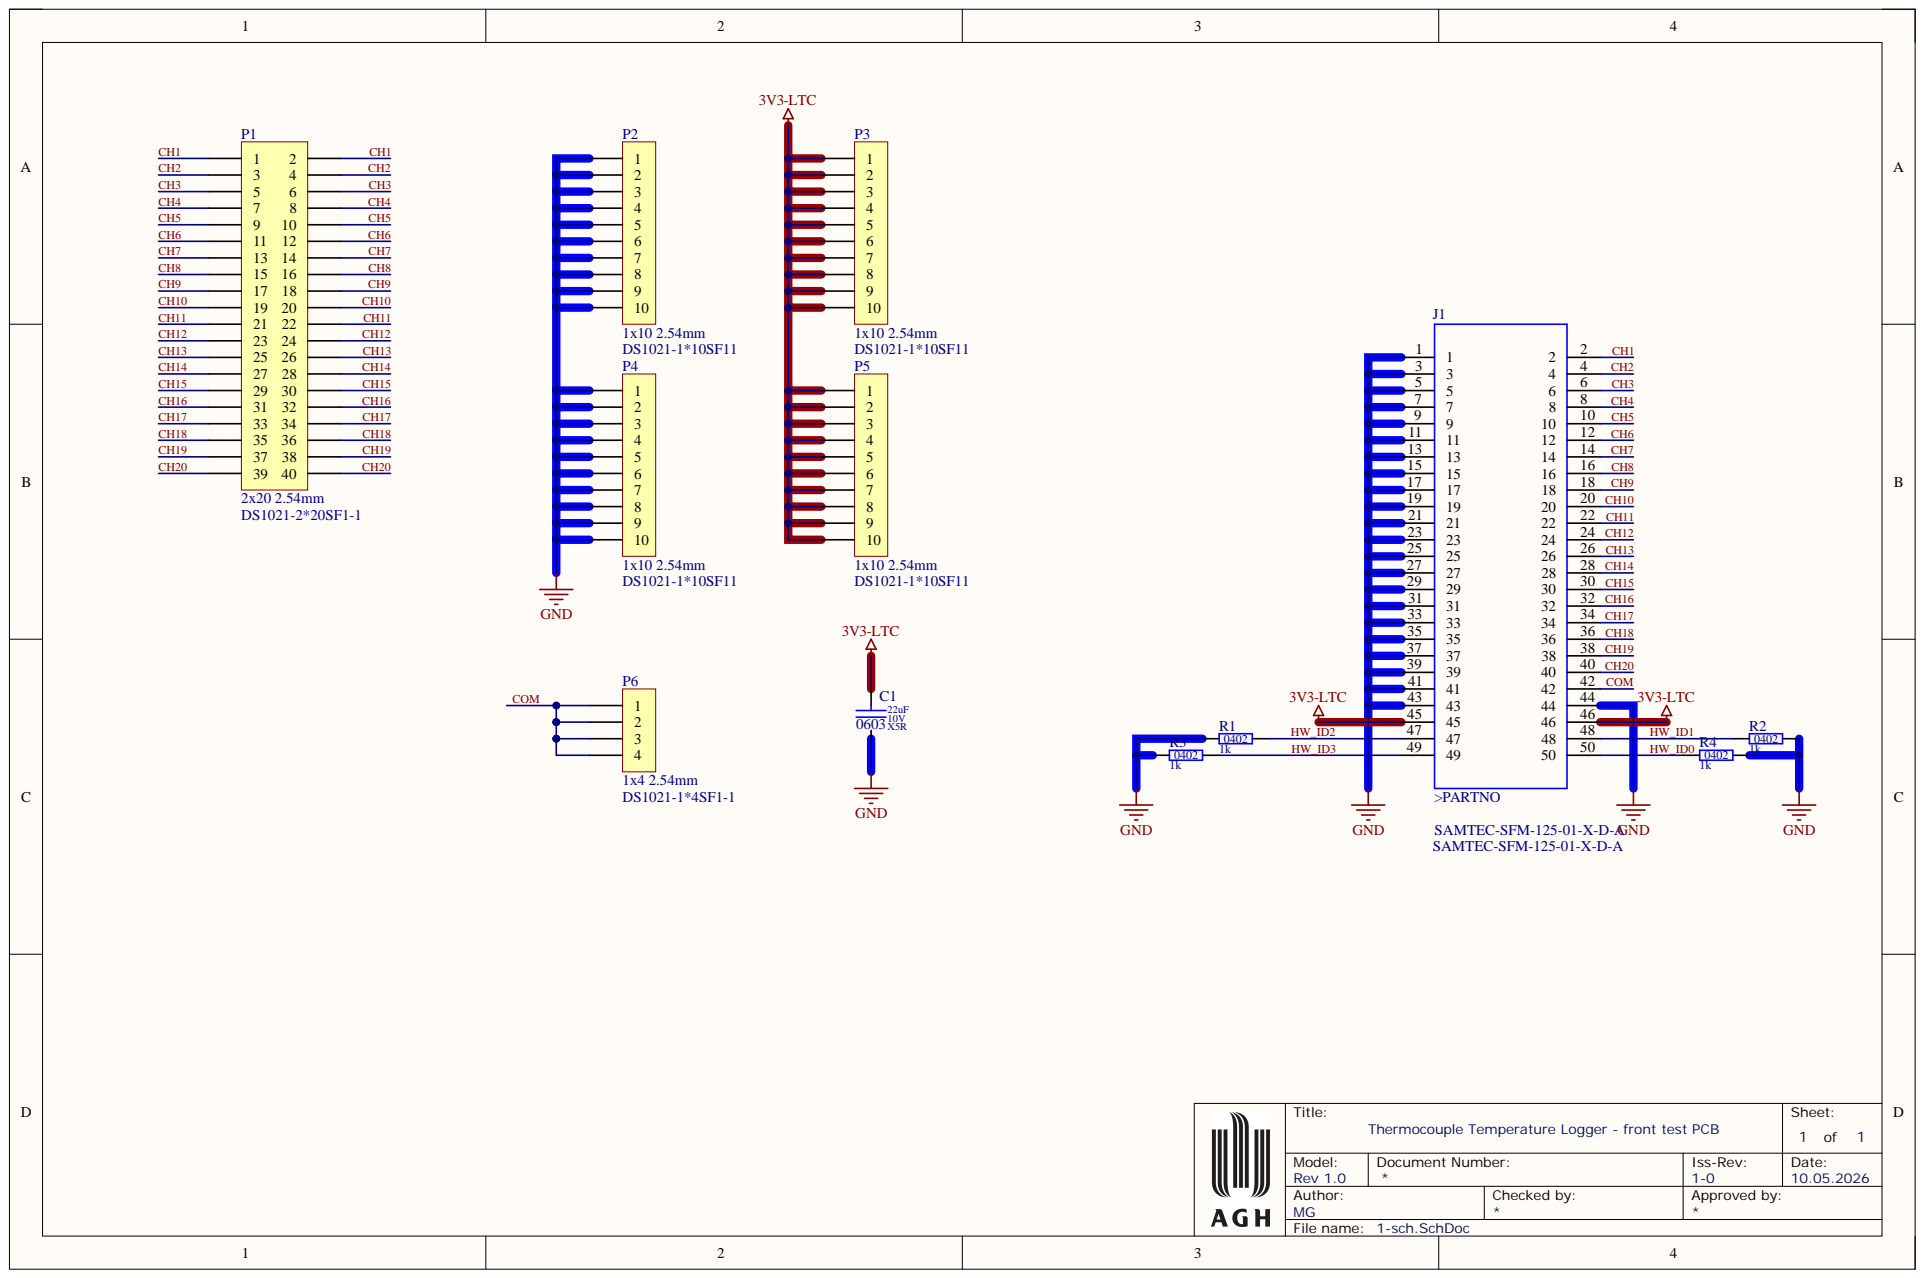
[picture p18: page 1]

7 | | 8 CH 4
9 | | CH 5
1 1 | | CH 6
13 13 | CH 7
15 15 | CH 8
17 17 | CH 9
19 19 | CH1 0
21 21 | CH1 1
23 23 | CH1 2
25 25 | CH1 3

29 29 | CH1 5
31 31 | CH1 6

35 35 | CH1 8
37 37 | CH1 9
39 39 | CH2 0
41 41 | CO M

Title: Thermocouple Temperature Logger - front test PCB | Sheet: 1 of 1

Model: | Document Number: * | Iss-Rev: | Date:
Rev 1.0 Author: MG | Checked by: | 1-0 * 10.05.2026 * Appro ved by:

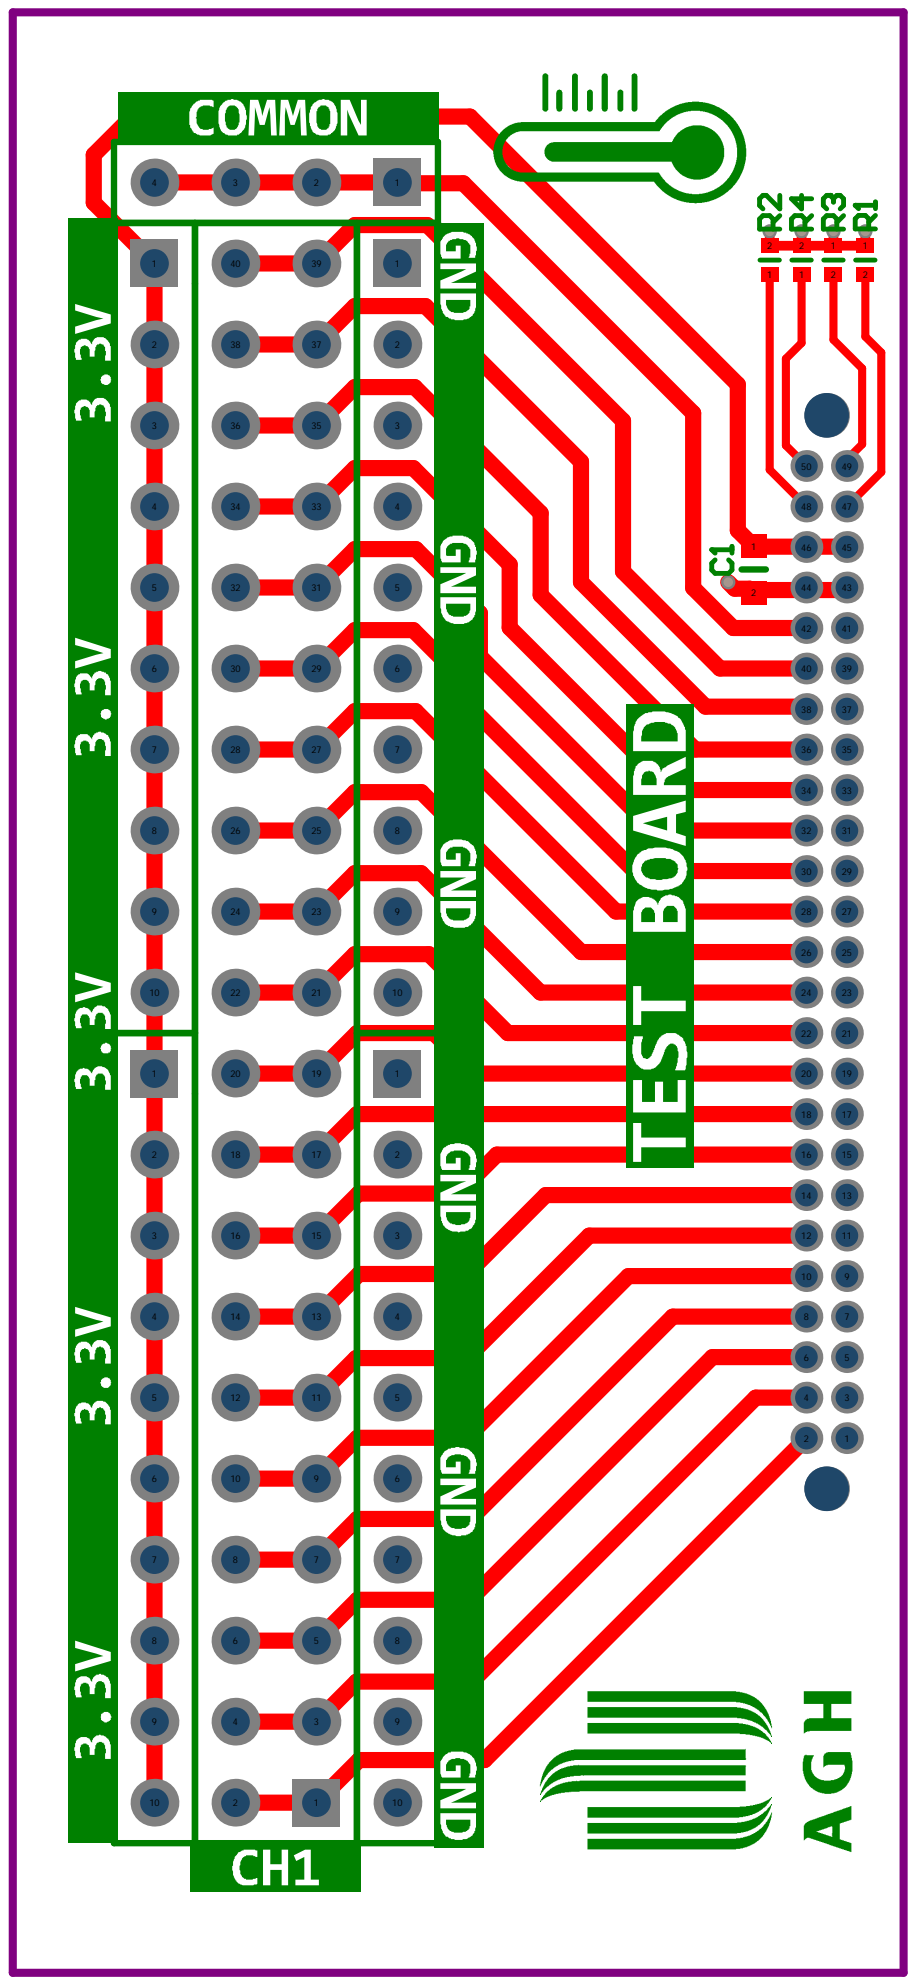
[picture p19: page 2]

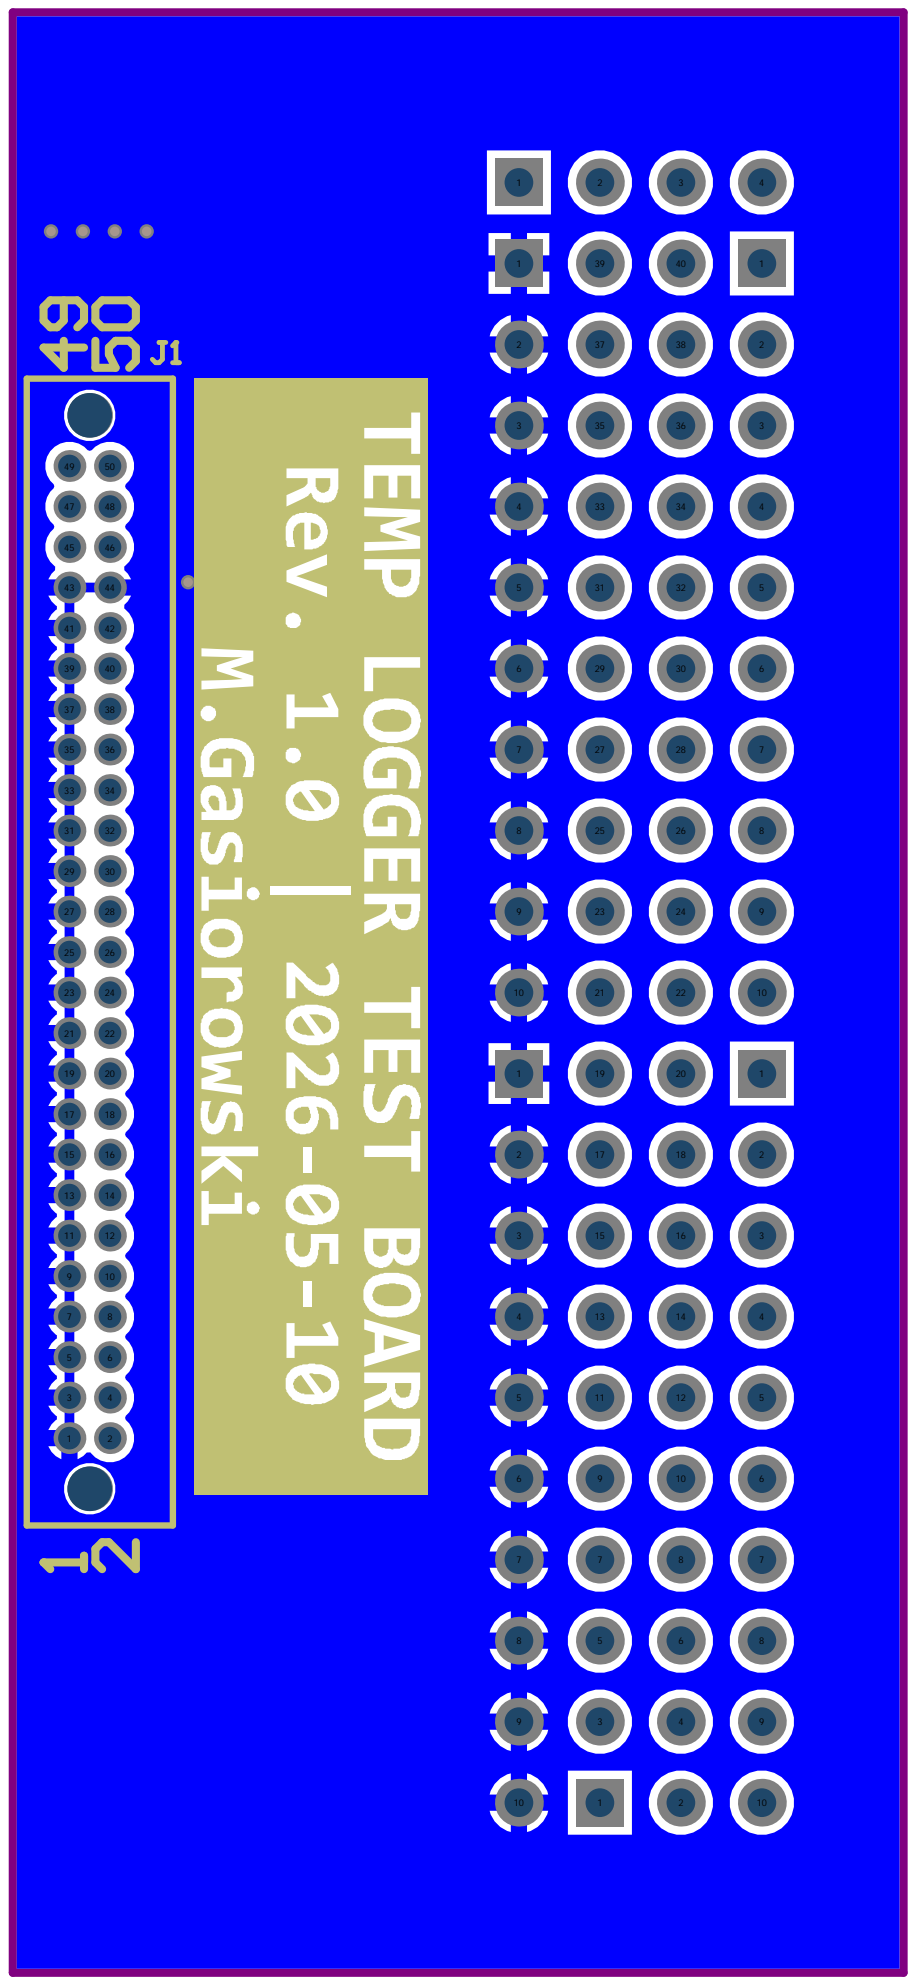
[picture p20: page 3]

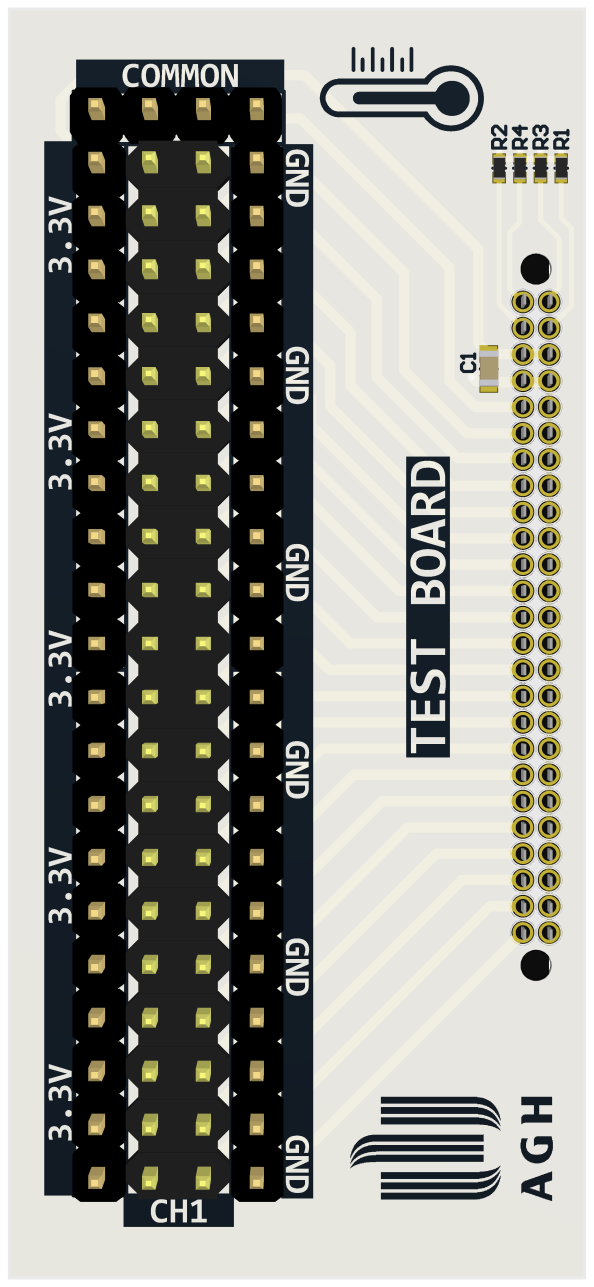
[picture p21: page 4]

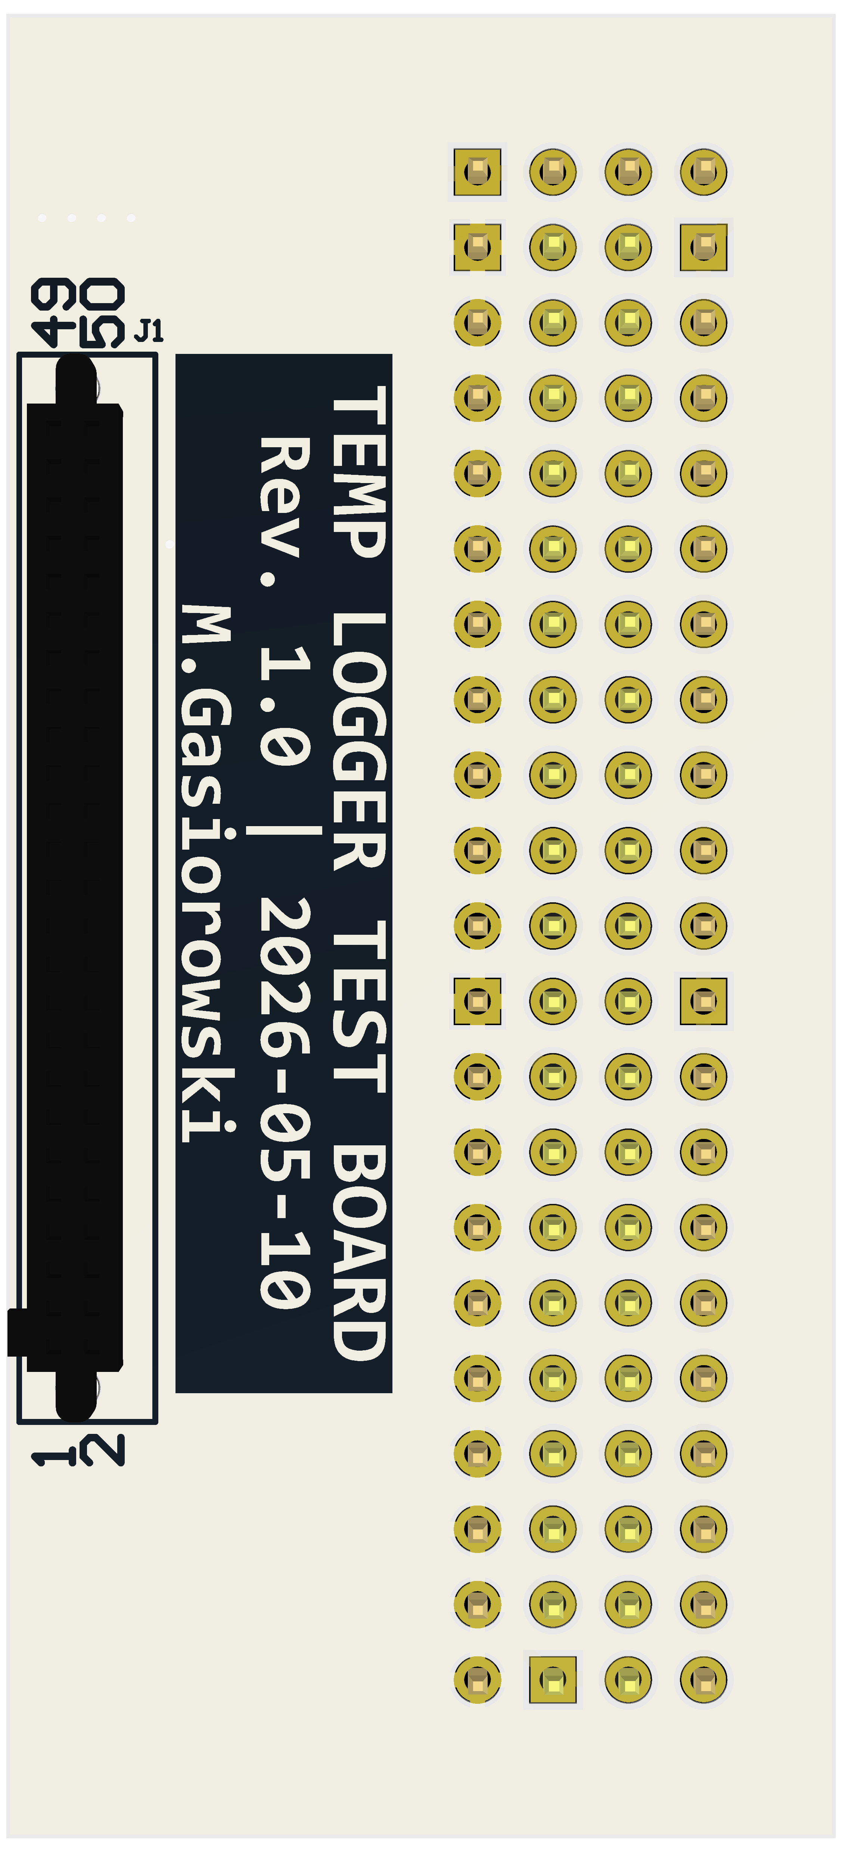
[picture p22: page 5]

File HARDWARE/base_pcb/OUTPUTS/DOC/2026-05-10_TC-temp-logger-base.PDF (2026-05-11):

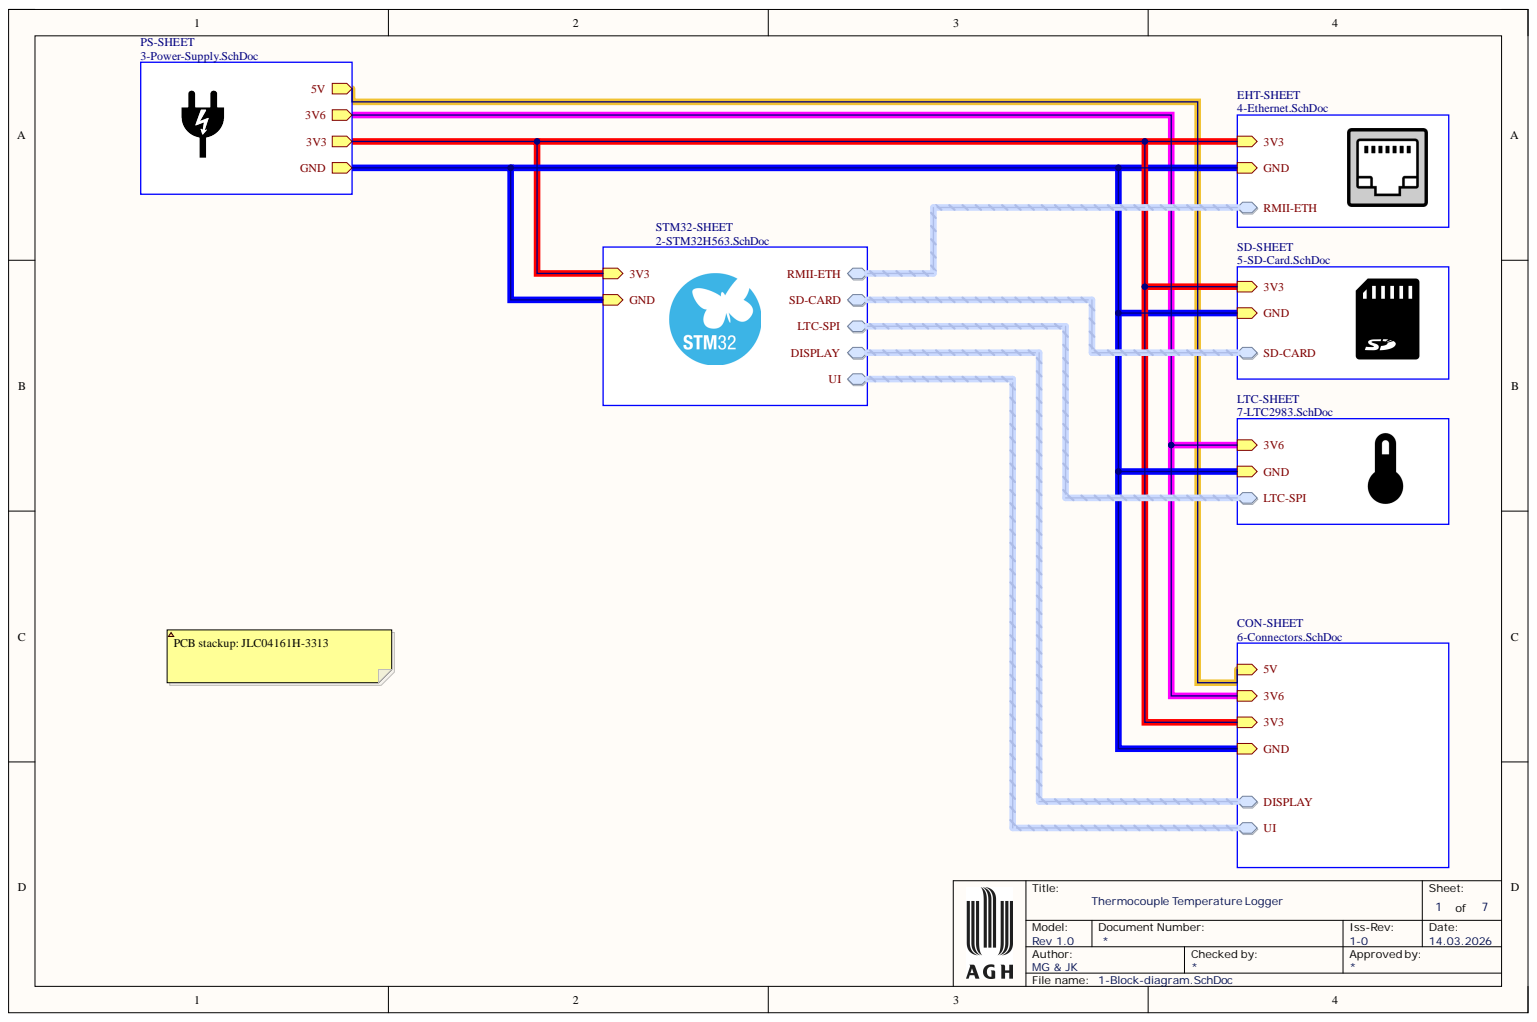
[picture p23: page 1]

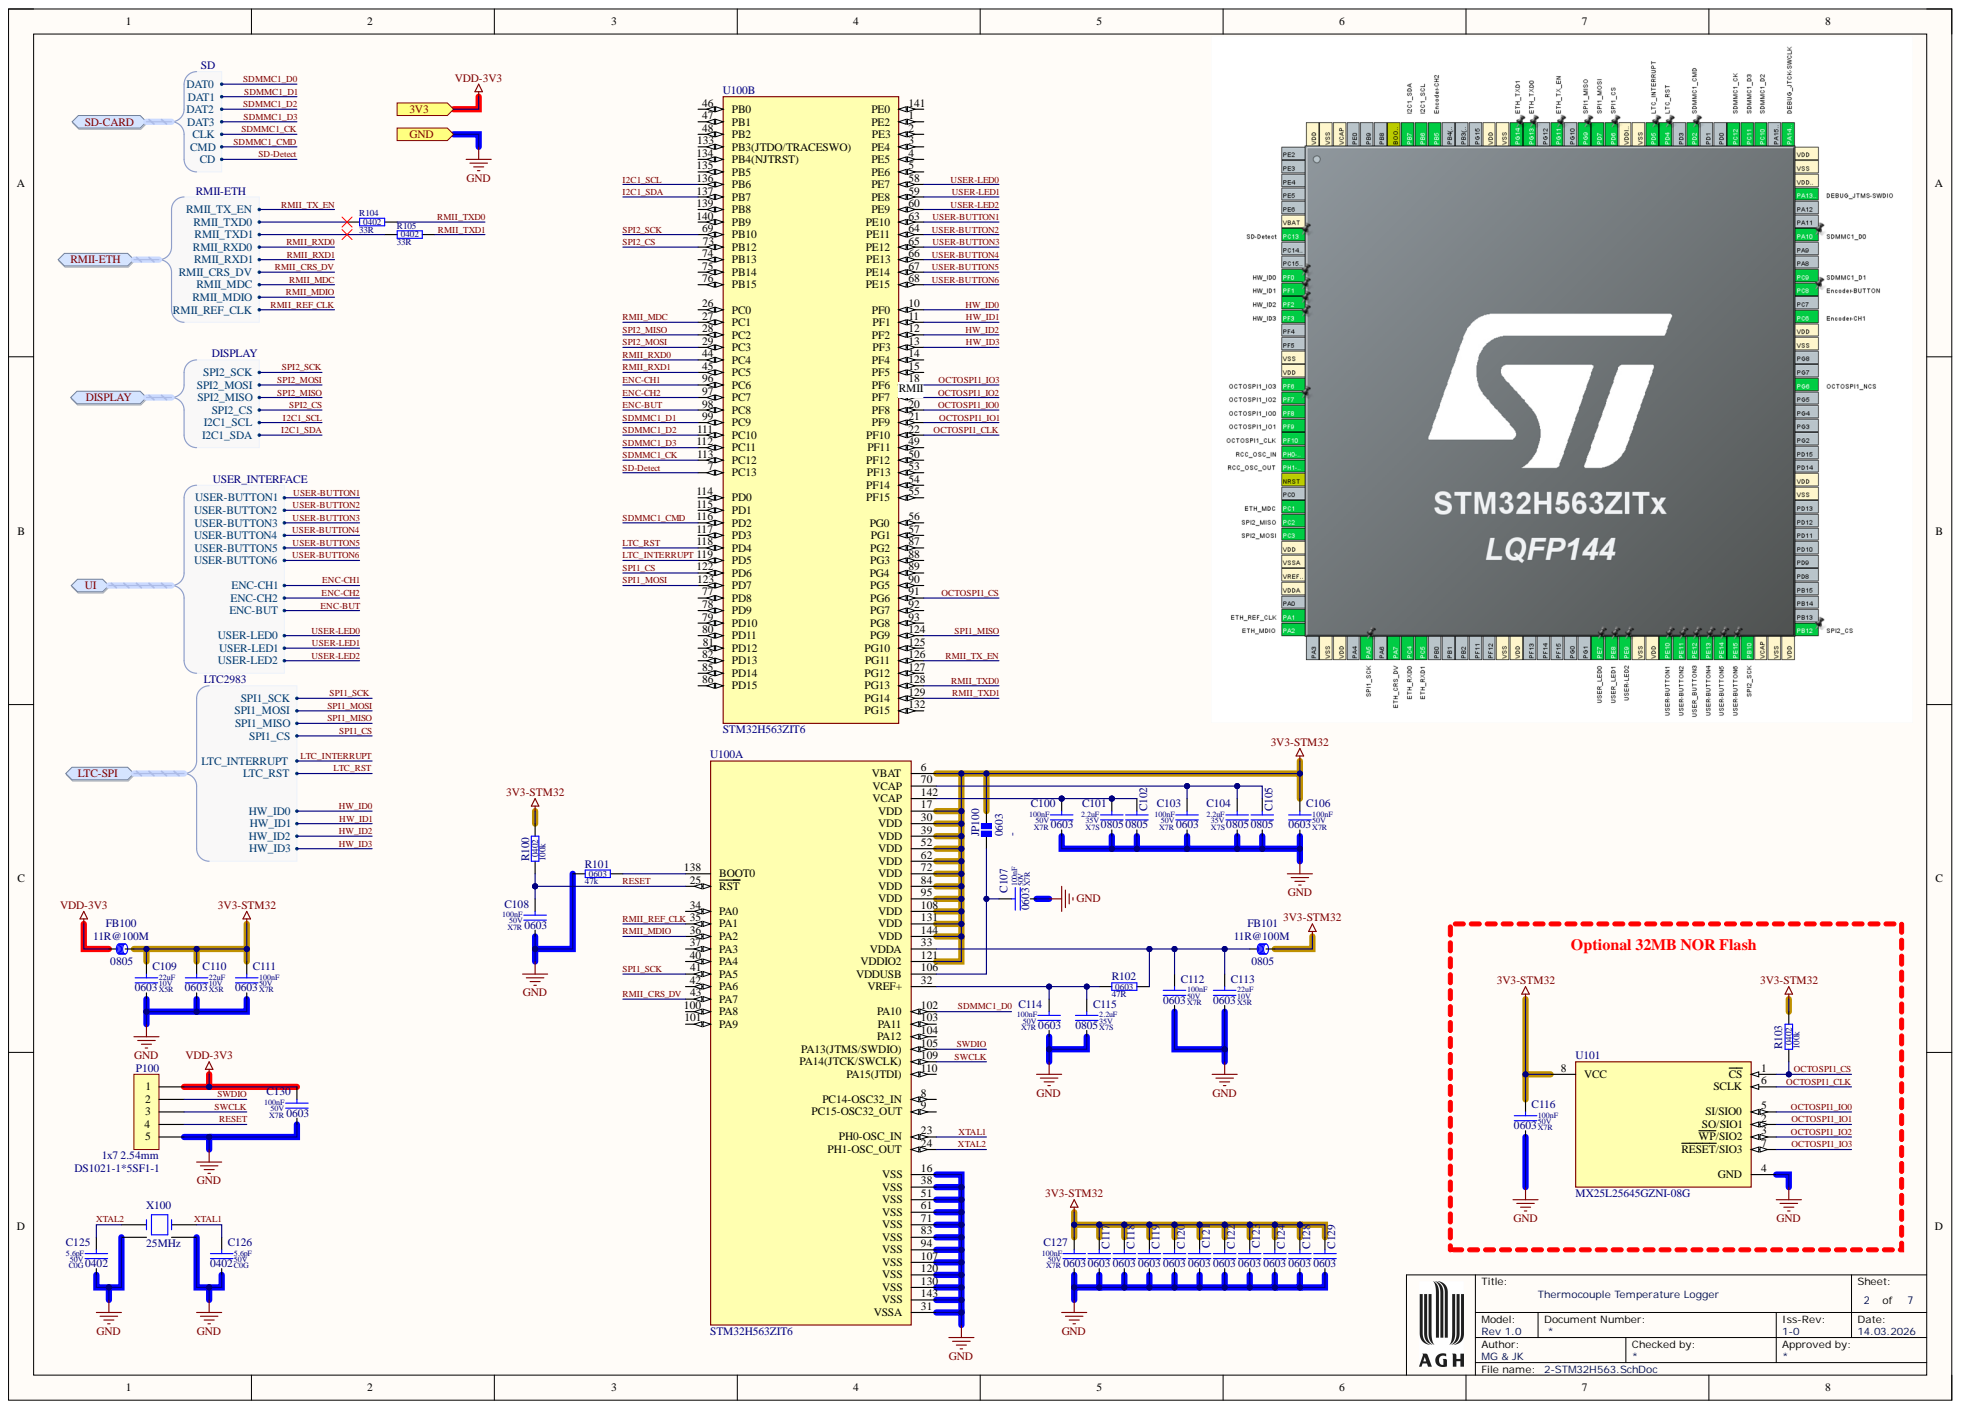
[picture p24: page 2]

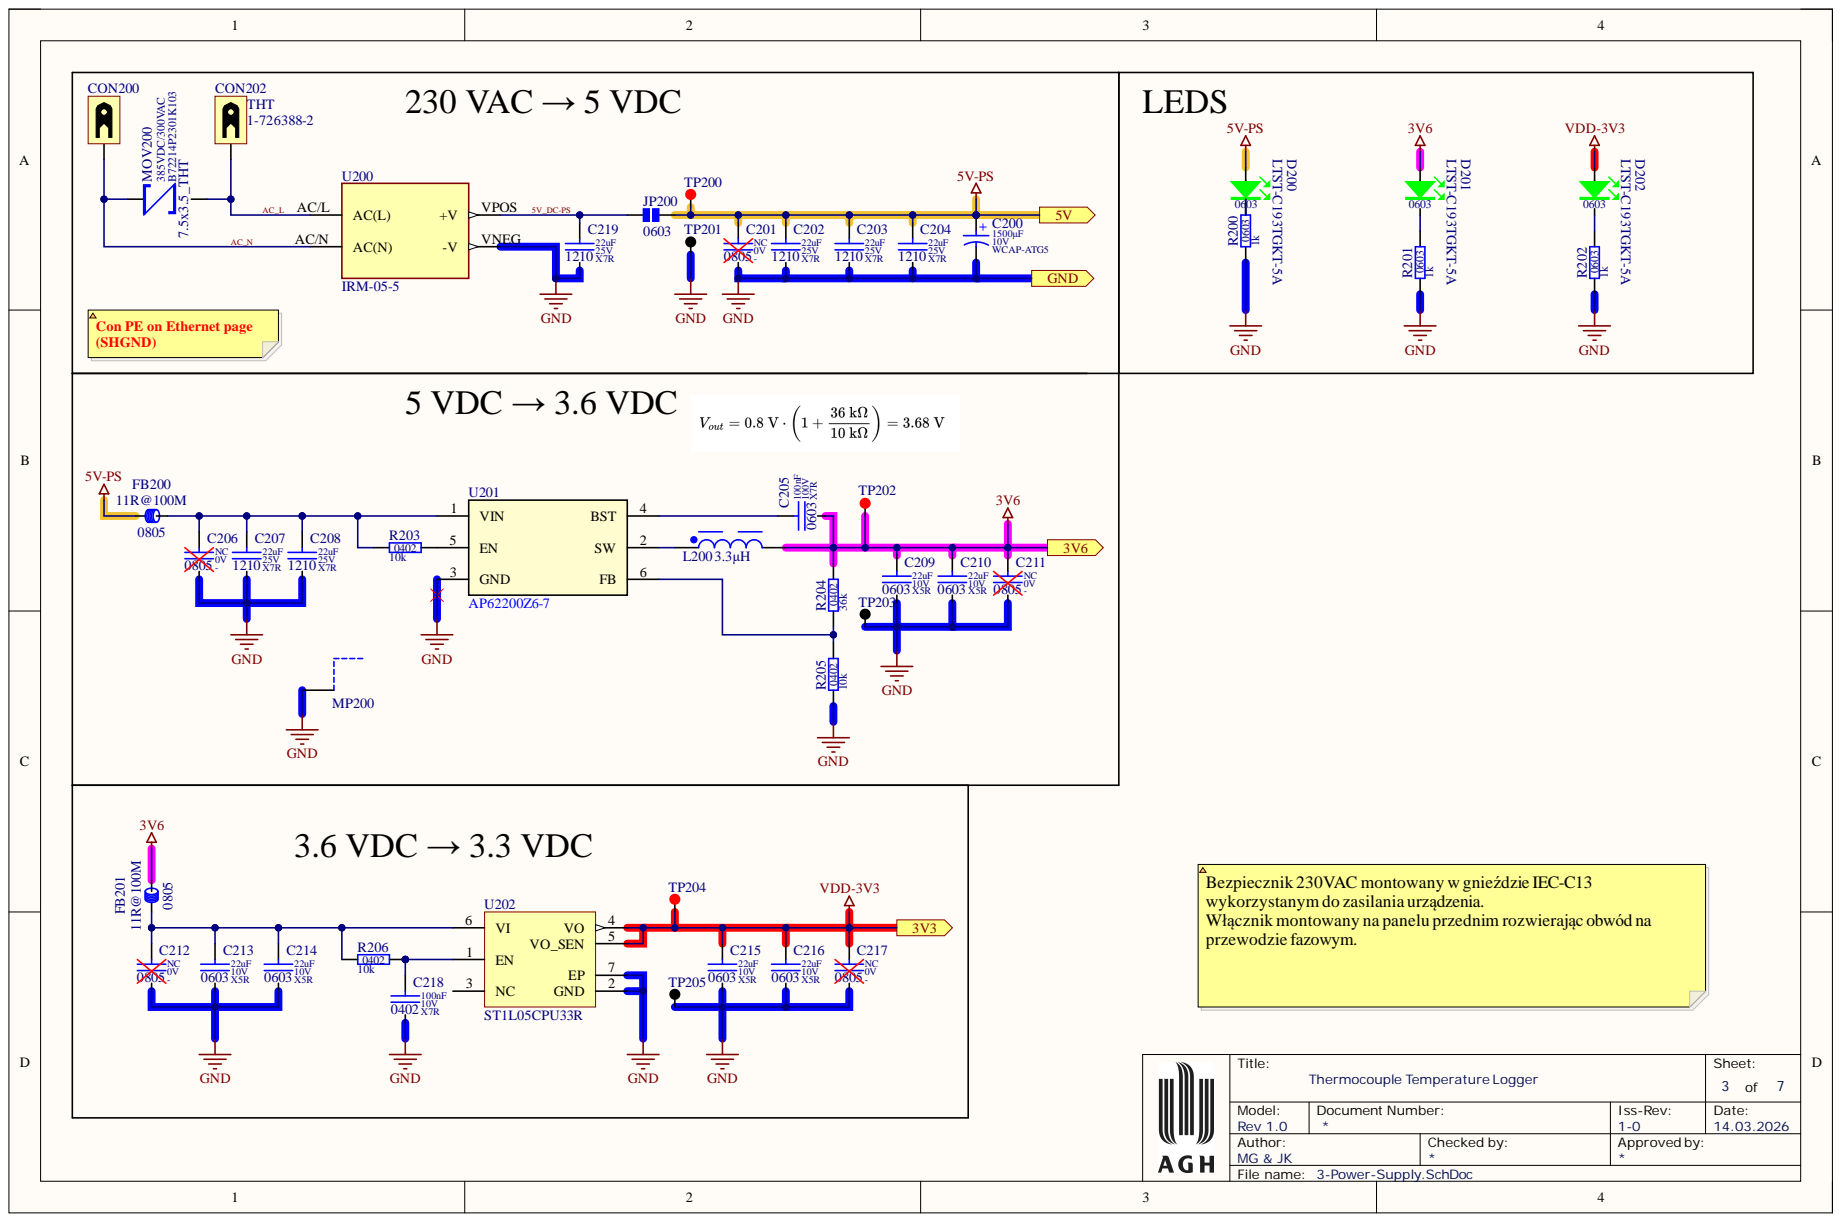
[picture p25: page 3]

Con PE on Ethernet page
(SHGND)

Bezpiecznik 230VAC montowany w gnieździe IEC-C13
wykorzystanym do zasilania urządzenia.
Włącznik montowany na panelu przednim rozwierając obwód na
przewodzie fazowym.

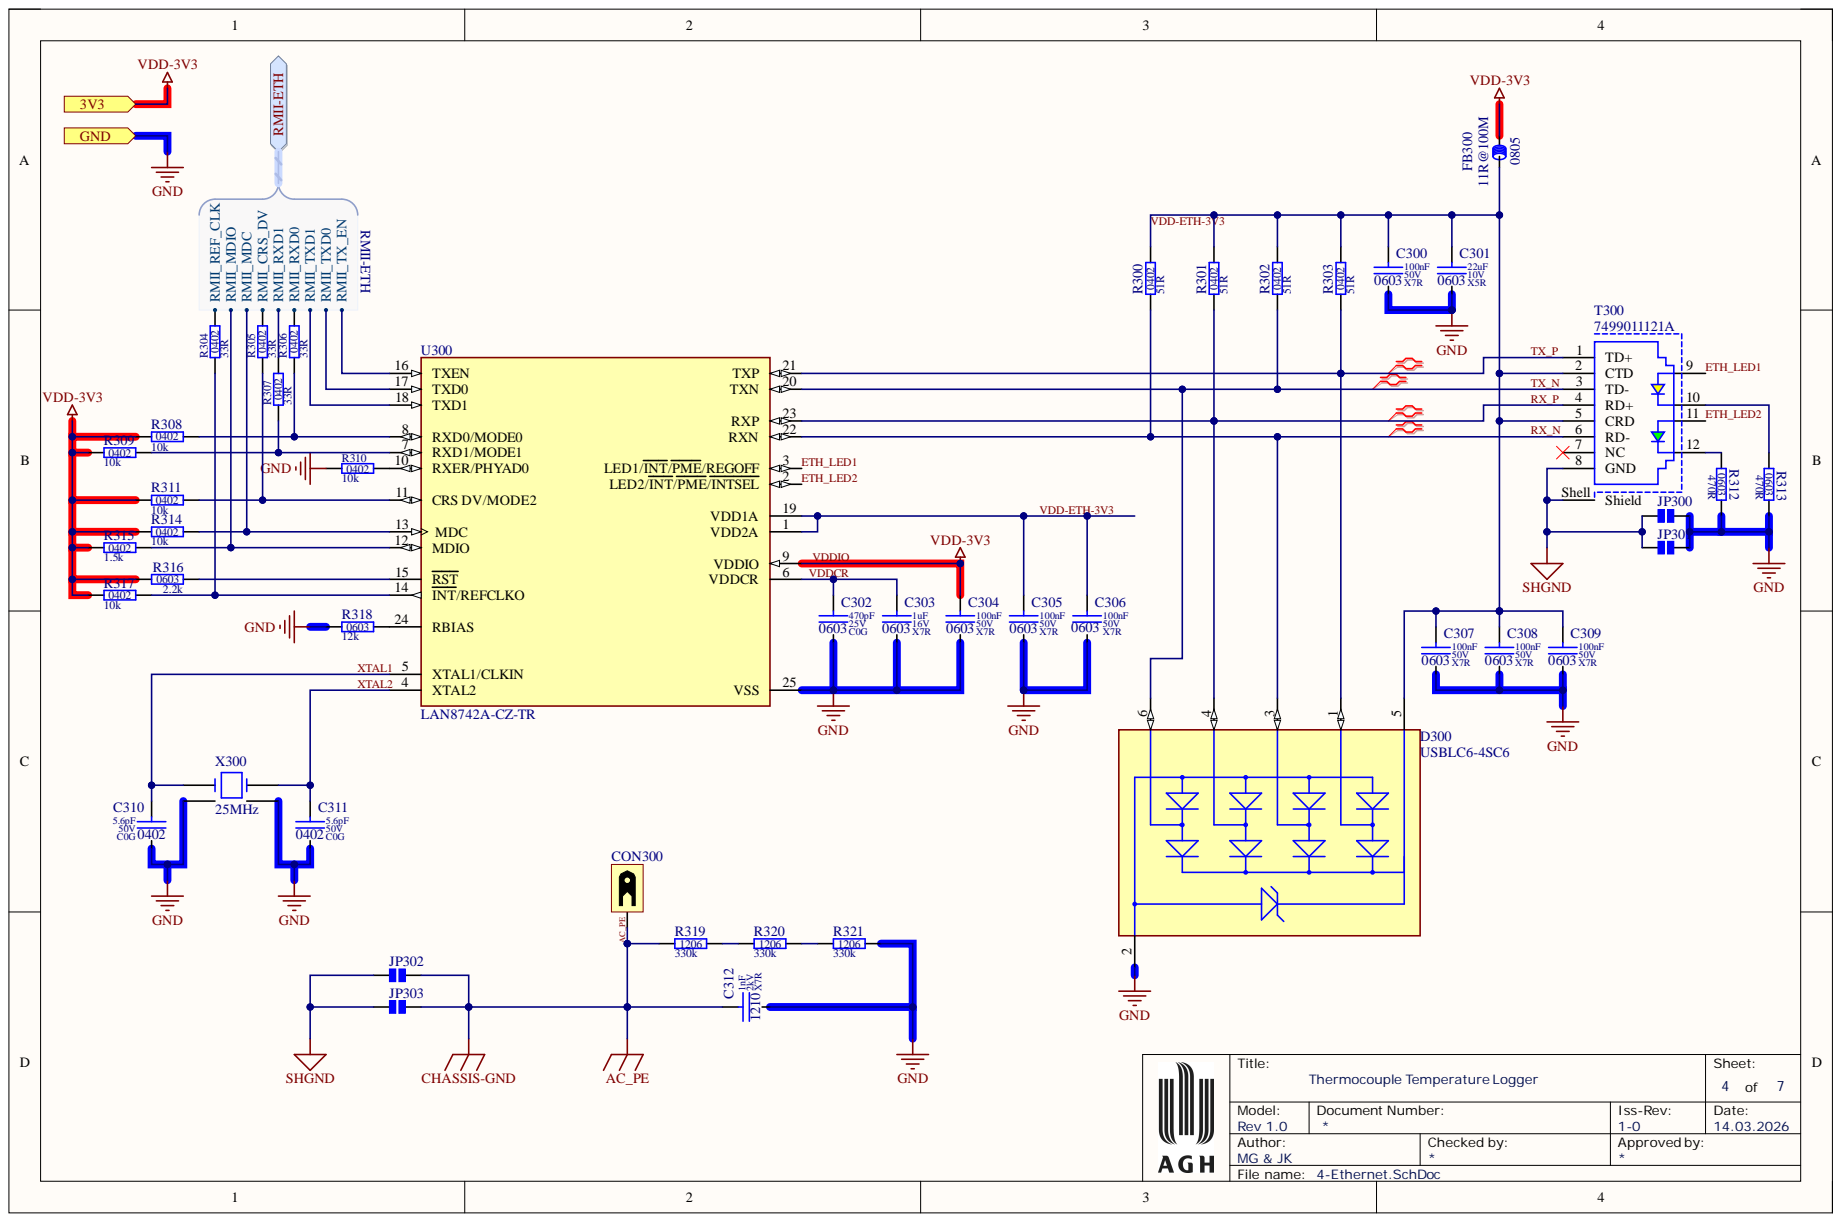
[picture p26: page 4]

R315 | | MDIO 12

R316 | INT/REFCLKO 14 RST 15

VDDCR

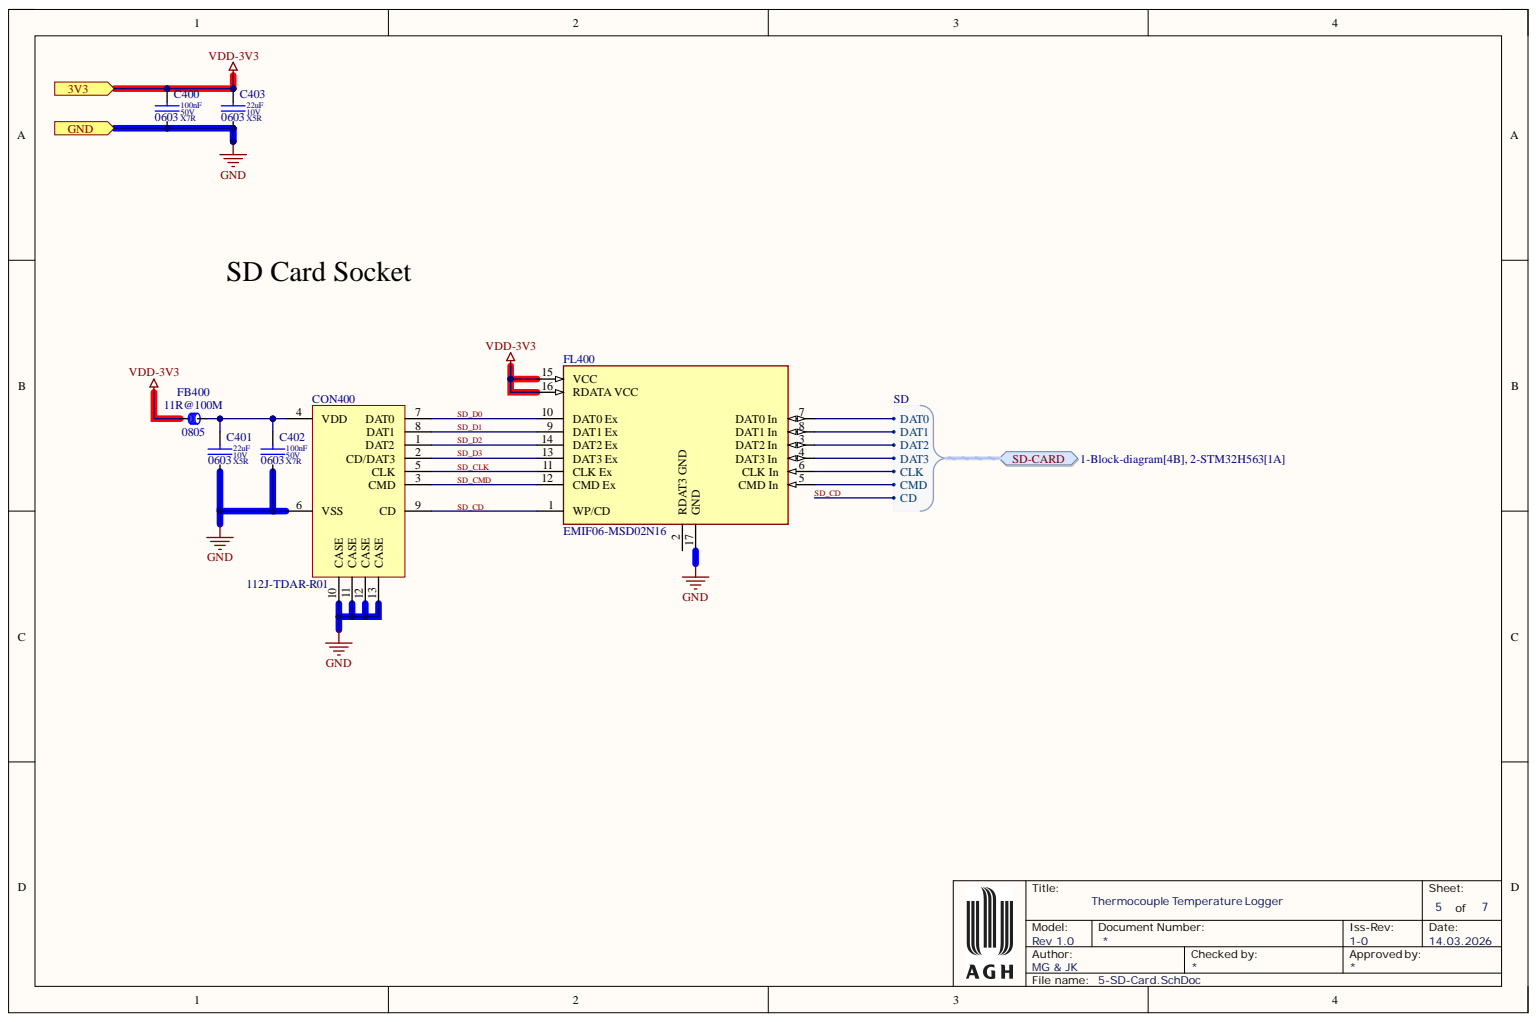
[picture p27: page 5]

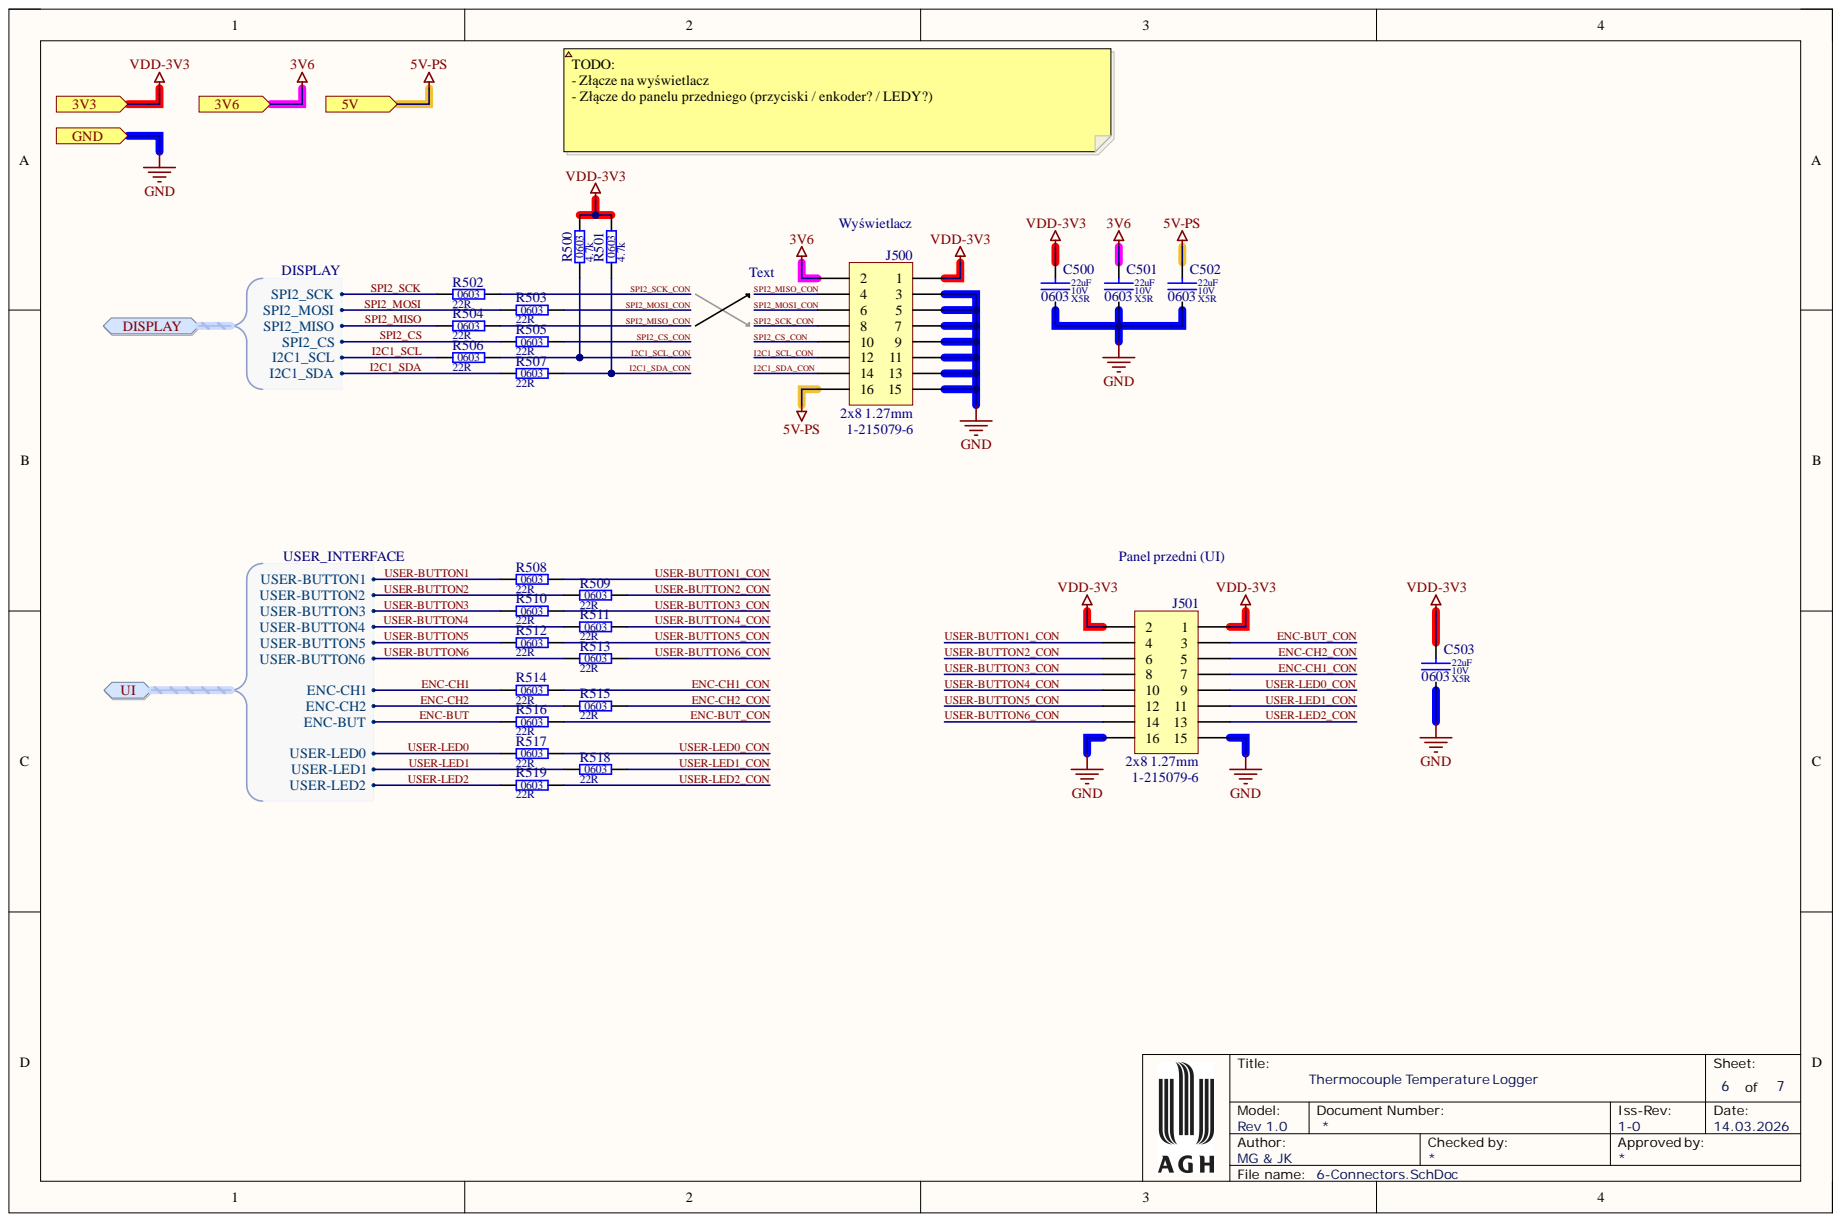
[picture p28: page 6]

TODO:
- Złącze na wyświetlacz
- Złącze do panelu przedniego (przyciski / enkoder? / LEDY?)

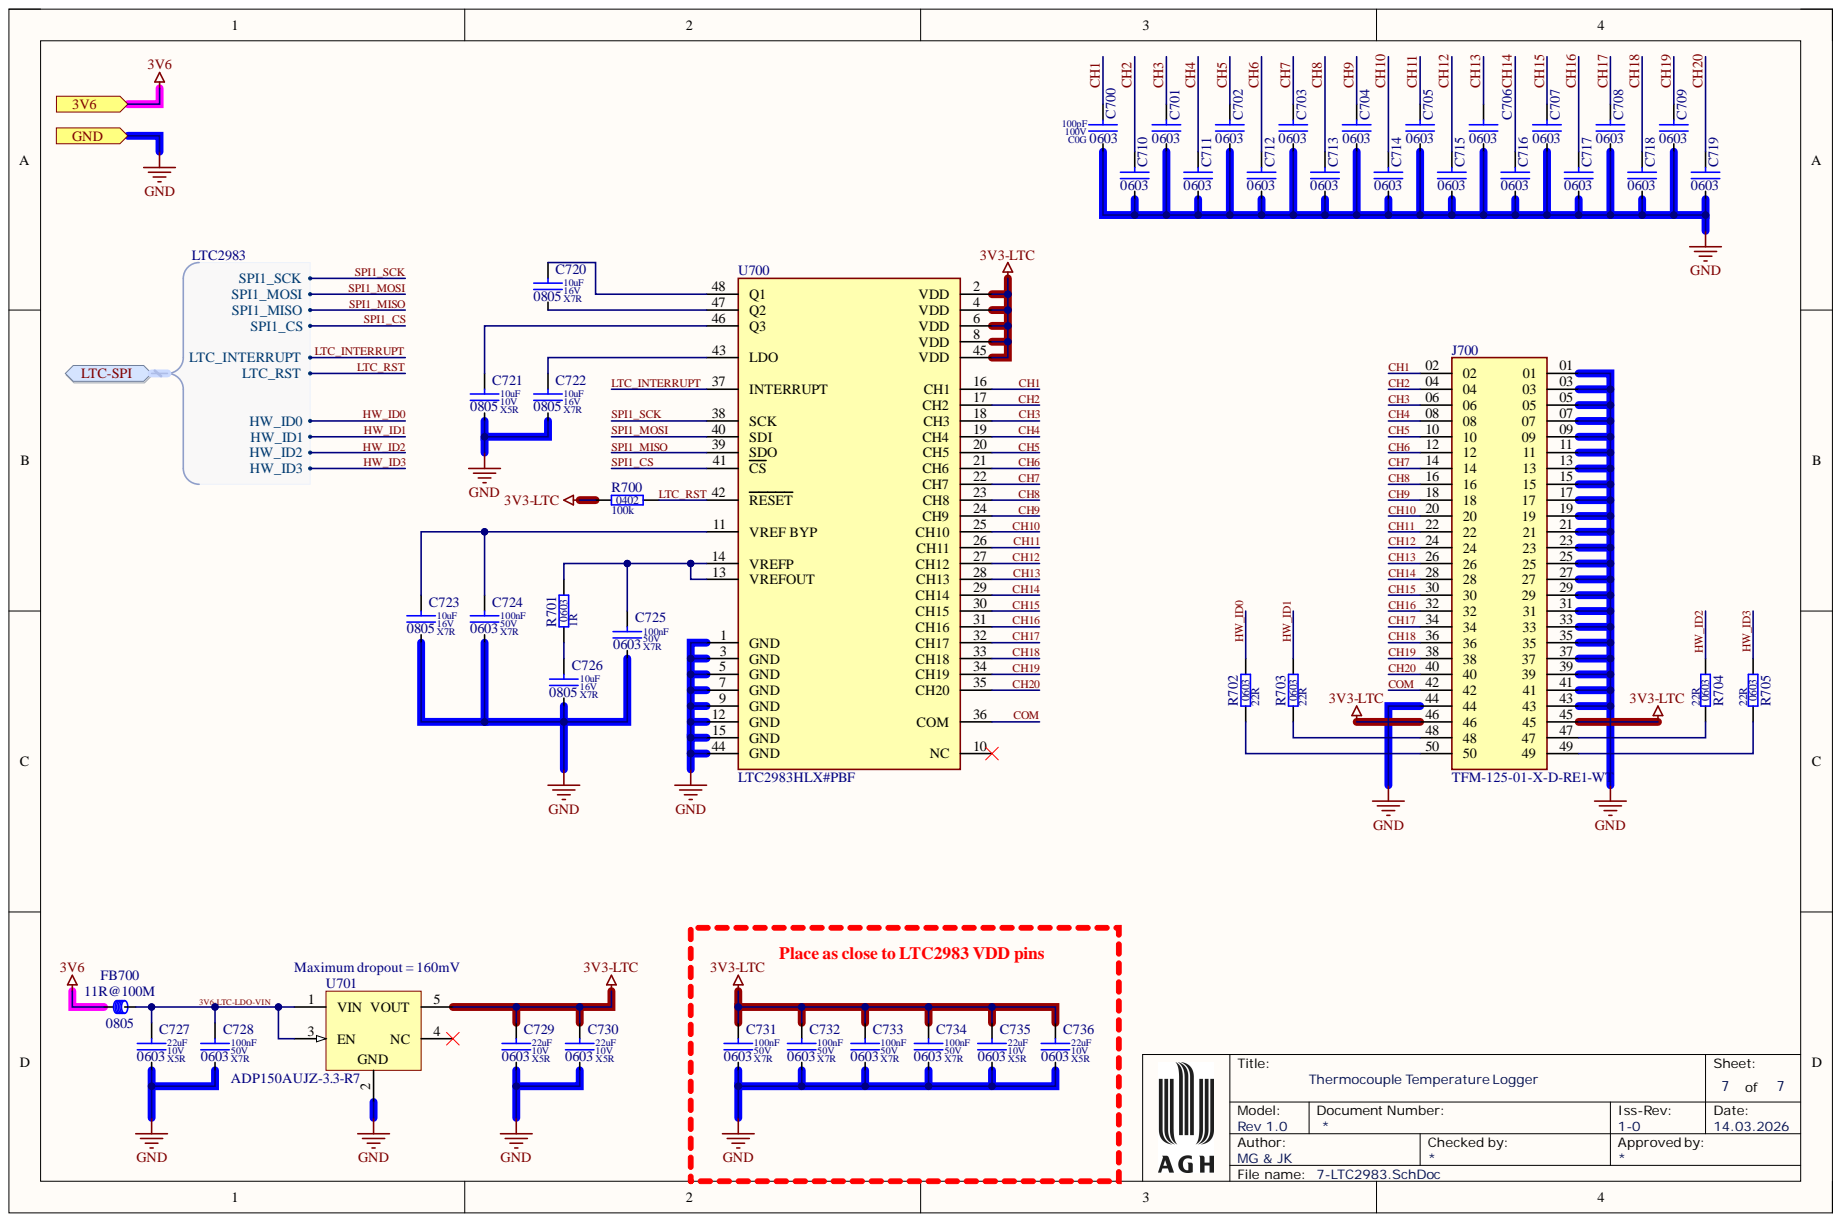
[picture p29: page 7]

Place as close to LTC2983 VDD pins







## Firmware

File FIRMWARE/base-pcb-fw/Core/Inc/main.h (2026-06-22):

/* USER CODE BEGIN Header */
/**
  ******************************************************************************
  * @file           : main.h
  * @brief          : Header for main.c file.
  *                   This file contains the common defines of the application.
  ******************************************************************************
  * @attention
  *
  * Copyright (c) 2026 STMicroelectronics.
  * All rights reserved.
  *
  * This software is licensed under terms that can be found in the LICENSE file
  * in the root directory of this software component.
  * If no LICENSE file comes with this software, it is provided AS-IS.
  *
  ******************************************************************************
  */
/* USER CODE END Header */

/* Define to prevent recursive inclusion -------------------------------------*/
#ifndef __MAIN_H
#define __MAIN_H

#ifdef __cplusplus
extern "C" {
#endif

/* Includes ------------------------------------------------------------------*/
#include "stm32h5xx_hal.h"

/* Private includes ----------------------------------------------------------*/
/* USER CODE BEGIN Includes */

/* USER CODE END Includes */

/* Exported types ------------------------------------------------------------*/
/* USER CODE BEGIN ET */

/* USER CODE END ET */

/* Exported constants --------------------------------------------------------*/
/* USER CODE BEGIN EC */

/* USER CODE END EC */

/* Exported macro ------------------------------------------------------------*/
/* USER CODE BEGIN EM */

/* USER CODE END EM */

/* Exported functions prototypes ---------------------------------------------*/
void Error_Handler(void);

/* USER CODE BEGIN EFP */

/* USER CODE END EFP */

/* Private defines -----------------------------------------------------------*/
#define LTC_INTERRUPT_Pin GPIO_PIN_5
#define LTC_INTERRUPT_GPIO_Port GPIOE
#define SD_Detect_Pin GPIO_PIN_13
#define SD_Detect_GPIO_Port GPIOC
#define HW_ID1_Pin GPIO_PIN_1
#define HW_ID1_GPIO_Port GPIOF
#define HW_ID2_Pin GPIO_PIN_2
#define HW_ID2_GPIO_Port GPIOF
#define HW_ID3_Pin GPIO_PIN_3
#define HW_ID3_GPIO_Port GPIOF
#define LD1_Pin GPIO_PIN_0
#define LD1_GPIO_Port GPIOB
#define USER_LED0_Pin GPIO_PIN_7
#define USER_LED0_GPIO_Port GPIOE
#define USER_LED1_Pin GPIO_PIN_8
#define USER_LED1_GPIO_Port GPIOE
#define USER_LED2_Pin GPIO_PIN_9
#define USER_LED2_GPIO_Port GPIOE
#define USER_BUTTON1_Pin GPIO_PIN_10
#define USER_BUTTON1_GPIO_Port GPIOE
#define USER_BUTTON2_Pin GPIO_PIN_11
#define USER_BUTTON2_GPIO_Port GPIOE
#define USER_BUTTON3_Pin GPIO_PIN_12
#define USER_BUTTON3_GPIO_Port GPIOE
#define USER_BUTTON4_Pin GPIO_PIN_13
#define USER_BUTTON4_GPIO_Port GPIOE
#define USER_BUTTON5_Pin GPIO_PIN_14
#define USER_BUTTON5_GPIO_Port GPIOE
#define USER_BUTTON6_Pin GPIO_PIN_15
#define USER_BUTTON6_GPIO_Port GPIOE
#define SPI2_CS_Pin GPIO_PIN_12
#define SPI2_CS_GPIO_Port GPIOB
#define Encoder_CH1_Pin GPIO_PIN_6
#define Encoder_CH1_GPIO_Port GPIOC
#define Encoder_CH2_Pin GPIO_PIN_7
#define Encoder_CH2_GPIO_Port GPIOC
#define Encoder_BUTTON_Pin GPIO_PIN_8
#define Encoder_BUTTON_GPIO_Port GPIOC
#define LTC_RST_Pin GPIO_PIN_4
#define LTC_RST_GPIO_Port GPIOD

/* USER CODE BEGIN Private defines */
#define USER_LED1_Pin GPIO_PIN_8
#define USER_LED1_GPIO_Port GPIOE
/* USER CODE END Private defines */

#ifdef __cplusplus
}
#endif

#endif /* __MAIN_H */

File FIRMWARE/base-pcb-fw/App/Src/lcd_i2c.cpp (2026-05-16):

#include "lcd_i2c.hpp"
#include <cstdarg>
#include <cstdio>

#define PIN_RS  0
#define PIN_RW  1
#define PIN_E   2
#define PIN_BL  3
#define PIN_D4  4
#define PIN_D5  5
#define PIN_D6  6
#define PIN_D7  7

#define MASK_BL (1 << PIN_BL)

static const uint8_t row_offsets[] = {0x00, 0x40};

static const uint8_t common_addrs[] = {0x27, 0x3F, 0x20, 0x38, 0x21, 0x3E};

LCD_I2C::LCD_I2C(I2C_HandleTypeDef* hi2c, uint8_t address)
    : _hi2c(hi2c), _addr(address << 1), _bl_mask(MASK_BL)
{
}

bool LCD_I2C::begin()
{
    _addr = _addr >> 1;

    bool found = false;
    for (auto a : common_addrs)
    {
        if (HAL_I2C_IsDeviceReady(_hi2c, a << 1, 1, 50) == HAL_OK)
        {
            _addr = a;
            found = true;
            break;
        }
    }

    if (!found)
    {
        for (uint32_t trial = 0; trial < 10; trial++)
        {
            if (HAL_I2C_IsDeviceReady(_hi2c, _addr << 1, 1, 50) == HAL_OK)
            {
                found = true;
                break;
            }
            HAL_Delay(10);
        }
    }

    if (!found)
        return false;

    _addr = _addr << 1;
    _bl_mask = MASK_BL;
    initSeq();
    return true;
}

void LCD_I2C::delay_us(uint32_t us)
{
    for (uint32_t i = 0; i < us * 64; i++)
        __NOP();
}

void LCD_I2C::pulseEnable(uint8_t data)
{
    uint8_t out = data | (1 << PIN_E);
    HAL_I2C_Master_Transmit(_hi2c, _addr, &out, 1, 100);
    delay_us(1);

    out = data & ~(1 << PIN_E);
    HAL_I2C_Master_Transmit(_hi2c, _addr, &out, 1, 100);
    delay_us(1);
}

void LCD_I2C::writeNibble(uint8_t nibble, bool rs)
{
    uint8_t data = _bl_mask;
    if (rs)
        data |= (1 << PIN_RS);

    if (nibble & 0x01) data |= (1 << PIN_D4);
    if (nibble & 0x02) data |= (1 << PIN_D5);
    if (nibble & 0x04) data |= (1 << PIN_D6);
    if (nibble & 0x08) data |= (1 << PIN_D7);

    pulseEnable(data);
}

void LCD_I2C::writeByte(uint8_t data, bool rs)
{
    writeNibble(data >> 4, rs);
    writeNibble(data & 0x0F, rs);
}

void LCD_I2C::command(uint8_t cmd)
{
    writeByte(cmd, false);
    delay_us((cmd <= 0x03) ? 1640 : 50);
}

void LCD_I2C::initSeq()
{
    HAL_Delay(50);

    writeNibble(0x03, false);
    delay_us(5000);
    writeNibble(0x03, false);
    delay_us(5000);
    writeNibble(0x03, false);
    delay_us(200);
    writeNibble(0x02, false);
    delay_us(100);

    command(0x28);
    command(0x08);
    command(0x01);
    delay_us(2000);
    command(0x06);
    command(0x0C);

    HAL_Delay(10);
}

void LCD_I2C::clear()
{
    command(0x01);
    delay_us(2000);
}

void LCD_I2C::home()
{
    command(0x02);
    delay_us(2000);
}

void LCD_I2C::setCursor(uint8_t col, uint8_t row)
{
    if (row >= LCD_ROWS) row = LCD_ROWS - 1;
    if (col >= LCD_COLS) col = LCD_COLS - 1;
    command(0x80 | (row_offsets[row] + col));
}

void LCD_I2C::print(const char* str)
{
    while (*str)
    {
        writeByte(*str, true);
        delay_us(50);
        str++;
    }
}

void LCD_I2C::printf(const char* fmt, ...)
{
    char buf[LCD_COLS + 1];
    va_list args;
    va_start(args, fmt);
    vsnprintf(buf, sizeof(buf), fmt, args);
    va_end(args);
    print(buf);
}

void LCD_I2C::backlight(bool on)
{
    _bl_mask = on ? MASK_BL : 0;
    uint8_t data = _bl_mask;
    HAL_I2C_Master_Transmit(_hi2c, _addr, &data, 1, 100);
}

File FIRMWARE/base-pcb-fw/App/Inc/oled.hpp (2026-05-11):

#ifndef OLED_HPP
#define OLED_HPP

#include "stm32h5xx_hal.h"

#define OLED_WIDTH  128
#define OLED_HEIGHT 64
#define OLED_COLS   128
#define OLED_PAGES  8
#define OLED_BUF_SIZE (OLED_COLS * OLED_PAGES)

class OLED
{
public:
    OLED(I2C_HandleTypeDef* hi2c, uint8_t address);

    void init();
    void clear();
    void clearBuffer();
    void update();

    void setPixel(uint8_t x, uint8_t y, bool on);
    void drawChar(uint8_t x, uint8_t y, char c);
    void drawString(uint8_t x, uint8_t y, const char* str);

    void sendCommand(uint8_t cmd);
    void sendBuffer();

private:
    I2C_HandleTypeDef* _hi2c;
    uint8_t _addr;
    uint8_t _buf[OLED_BUF_SIZE];
};

#endif

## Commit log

2026-03-17 added power supply requirements for README.md
2026-03-18 initial base pcb size and enclosure defined
    [1-Block-diagram.SchDoc, TC-temp-logger-base.PcbDoc, TC-temp-logger-base.PrjPcb, ZR185_180_65_step.step]
2026-04-03 added IC / connectors to schematic and lib
    [1-Block-diagram.SchDoc, 2-STM32H563.SchDoc, 3-Power-Supply.SchDoc, 4-Ethernet.SchDoc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]
2026-04-03 imported changes to PCB
    [TC-temp-logger-base.PcbDoc]
2026-04-08 power sch done, update lib
    [2-STM32H563.SchDoc, 3-Power-Supply.SchDoc, 4-Ethernet.SchDoc, 5-SD-Card.SchDoc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]
2026-04-09 add cubemx pins and initial ETH schematic
    [2-STM32H563.SchDoc, 4-Ethernet.SchDoc]
2026-04-09 moved .ioc to FW, added proper STM32H563 (diffrent MPN, without SMPS)
    [2-STM32H563.SchDoc, 4-Ethernet.SchDoc, TC-temp-logger-base.PrjPcb]
2026-04-09 sync SCH → PCB
    [TC-temp-logger-base.PcbDoc]
2026-04-09 add ETH schematic
    [2-STM32H563.SchDoc, 4-Ethernet.SchDoc]
2026-04-12 configured STM32H563 project
2026-04-12 refactor 3-power-supply schematic
    [3-Power-Supply.SchDoc]
2026-04-14 fix PSU cap conn, add SD card schematic, add card detect GPIO pin in cubemx
    [2-STM32H563.SchDoc, 3-Power-Supply.SchDoc, 5-SD-Card.SchDoc]
2026-04-15 added EMIF06-MSD02N16 to SD-CARD, SD-Card Harness, changed 230VAC connector to 4.8mm tabs.
    [1-Block-diagram.SchDoc, 2-STM32H563.SchDoc, 3-Power-Supply.SchDoc, 4-Ethernet.SchDoc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]
2026-04-16 correction of block diagram sch, added harnesses, corrected eth sch
    [1-Block-diagram.SchDoc, 2-STM32H563.SchDoc, 3-Power-Supply.SchDoc, 4-Ethernet.SchDoc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]
2026-04-16 addapted project for strict hierarchical
    [1-Block-diagram.SchDoc, 2-STM32H563.SchDoc, 3-Power-Supply.SchDoc, 4-Ethernet.SchDoc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]
2026-04-16 pins swaps in IOC ans started work on STM32H5 sch. Added LEDs to Power Supply schematic as indicators. Sync SCH → PCB
    [2-STM32H563.SchDoc, 3-Power-Supply.SchDoc, 5-SD-Card.SchDoc, TC-temp-logger-base.PcbDoc]
2026-04-16 added note to Power supply sch about fuse and on/off switch
    [3-Power-Supply.SchDoc]
2026-04-17 schematics wip
    [1-Block-diagram.SchDoc, 2-STM32H563.SchDoc, 3-Power-Supply.SchDoc, 6-Connectors.SchDoc]
2026-05-03 reconfigured stm32h5 ioc to include all perypherials, sync with sch
    [2-STM32H563.SchDoc, 5-SD-Card.SchDoc, 6-Connectors.SchDoc]
2026-05-06 finished sch (moved LTC to base_PCB), PCB early placement
    [1-Block-diagram.SchDoc, 2-STM32H563.SchDoc, 3-Power-Supply.SchDoc, 4-Ethernet.SchDoc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]
2026-05-06 proto component placement done, routing todo
    [2-STM32H563.SchDoc, 3-Power-Supply.SchDoc, 4-Ethernet.SchDoc, 7-LTC2983.SchDoc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]
2026-05-09 fixed nets name (not connected net-label), LTC and Ethernet routed
    [1-Block-diagram.SchDoc, 2-STM32H563.SchDoc, 4-Ethernet.SchDoc, 7-LTC2983.SchDoc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]
2026-05-10 Schematic minor tuninng (pin swapping, more decoupling capacitors). PCB early done DRC pass (without silkscreen (TODO)),
    [2-STM32H563.SchDoc, 3-Power-Supply.SchDoc, 4-Ethernet.SchDoc, 5-SD-Card.SchDoc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]
2026-05-10 pcb polishing (without silkscreen), added MOV to 230VAC input
    [3-Power-Supply.SchDoc, TC-temp-logger-base.PcbDoc]
2026-05-10 PCB polishing, Silkscreen (designators) done, more vias, minor fixes
    [TC-temp-logger-base.PcbDoc]
2026-05-10 PCB silk finished
    [TC-temp-logger-base.PcbDoc]
2026-05-10 finished PCB, silk done
    [TC-temp-logger-base.PcbDoc]
2026-05-10 finished PCB V2 :0
    [TC-temp-logger-base.PcbDoc]
2026-05-10 gerber done
    [TC-temp-logger-base.PcbDoc]
2026-05-10 added pdf with PCB docs
2026-05-10 added test front board - for eval purpose
    [1-sch.SchDoc, front_test_pcb.PcbDoc, front_test_pcb.PrjPcb]
2026-05-10 added changes of not saved before commit prjpcb
    [front_test_pcb.PrjPcb]
2026-05-16 threadX configuration
2026-05-17 add lcd thread and 8 termocouple id's
2026-06-04 5V→3.6V converter fix bst cap fix, 3.3V TP silkscreen fix
    [3-Power-Supply.SchDoc, TC-temp-logger-base.PcbDoc]
